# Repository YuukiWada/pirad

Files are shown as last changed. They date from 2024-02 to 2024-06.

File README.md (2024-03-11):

# PiRAD

## Overview
PiRAD is a radiation detector using Raspberry Pi. It allows for the acquisition of information for each photon of X-rays and gamma rays (energy and arrival time), as well as functions such as supplying high voltage for MPPCs (Multi-Pixel Photon Counters) and temperature compensation for MPPCs, all while being inexpensive and simple.

This software and design information are distributed under the GPL (GNU General Public License version 3). The developer bears no responsibility for any troubles, losses, or damages arising from the use of this software or design information.

## Usage
PiRAD consists of an analog circuit board that is stacked on the Raspberry Pi and software that runs on the Raspberry Pi.

### Things to prepare
- Raspberry Pi 4B+ (any memory capacity allowed)
- PiRAD board
- MPPC/SiPM, Scintillator, Coaxial cable
- AC adapter of 5 V and >2 A
- microSD card (16 GB or higher, Class 10 recommended)
- USB memory

### Circuit board
The `circuit` directory contains Gerber files and parts lists needed to fabricate a PCB board. Please use this information to produce the PCB board and mount the components on the board. The PCB board is a 4-layer board with dimensions of 105 mm x 56 mm. A disposable board is attached so that it can be fed into a chip mounter. V-cut is required. A reference marker for the chip mounter is also placed.

LT3482IUDTRPBF is used as the HV supplier chip. Please note that this chip has pads for surface mounting on the back side of the component, so placing components by a chip mounter may be required. In that case, it is necessary to manufacture a metal mask, which requires initial costs and is expensive if produced in small quantities. An effective method for small-volume production is to manufacture the boards without LT3482IUDTRPBF, and then manually mount it later manually. However, this is only possible if you have the technology to perform surface mounting using a heat gun and solder paste.

### Radiation detection section
This part is left to the user's choice. In the author's test environment, Hamamatsu's MPPC/SiPM S13360-6050CS is used, and a 1 x 1 x 1 cm GAGG scintillator is attached to the MPPC. The HV supply mounted on the circuit board has positive polarity, so supply voltage to the cathode and connect the anode to GND. In the author's environment, the MPPC is connected to the circuit board using a coaxial cable with an SMA terminal.

### Data Acquisition Software
The data acquisition software is stored in `scripts`. They consist of three languages: C, Python, and Ruby. Software operation has been confirmed on Raspberry Pi4 Model B and Raspberry Pi OS with Desktop 32-bit brookworm. 64-bit OS is not supported.

Please refer to `INSTALL.md` for how to set up the software.

### Radiation data acquisition
Once you have finished configuring the software, write the configuration file to a USB memory and insert it to the Raspberri Pi. Please refer to `INSTALL.md` for the configuration file settings.

After inserting the USB and turning on the Raspberry Pi, the PWR LED will light up. Observation can begin after the PWR LED turns on. By turning on the LOGGING slide switch, the USB memory will be mounted and observation will begin. If the USB memory cannot be read or is not correctly mounted, the LOG LED will blink twice.

If the USB memory is mounted successfully and the configuration file is also successfully read, the HV/LOG LED will light up and measurement will begin. If radiation is detected, the RAD LED will blink.

When a GPS module is connected and time synchronization is set, the GPS LED will light up while the time is synchronized by GPS acquisition.

To stop measurement, turn off the LOGGING slide switch. The HV/LOG LED will turn off within a few seconds. After that, the LOG LED will blink 5 times and the USB will be unmounted and you can safely remove it from the Raspberry Pi.

To shut down, press and hold the PWR OFF switch until the PWR LED turns off. Wait a few seconds for the shutdown process to complete. Please note that if you stop the power supply without performing the shutdown process, the SD card may not be read properly and you may not be able to start it up again.

### data format
Data is recorded in USB memory. Radiation data is recorded as text in CSV format, and the file name is the measurement start time (UTC). Inside the file is recorded as follows.
````
1710139818.021942
0.000070, 410
0.395692, 73
1.175464, 88
1.209030, 88
1.948140, 94
2.283456, 67
2.334519, 144
````
 The first line is the reference time (UNIXTIME), the second and subsequent lines correspond to the detected radiation event, the first column is the elapsed time (seconds) from the reference time, and the second column is the peak value (pulse height). Conversion from peak value to energy requires calibration using a radiation source, etc. The files are separated by day and are switched around 0:00 UTC (9:00 Japan Standard Time / JST).

HK (housekeeping) data is also saved with the recording start time as the file name, and is recorded as follows.

````
1706767240, 2024-02-01 06:00:40, 54.49946, 24.99, 30.12, 1011.96
1706767540, 2024-02-01 06:05:40, 54.49946, 24.83, 30.36, 1011.89
1706767840, 2024-02-01 06:10:40, 54.49946, 24.77, 30.31, 1011.87
1706768140, 2024-02-01 06:15:40, 54.49946, 24.91, 30.12, 1011.88
````
The first column is UNIXTIME, the second column is the corresponding time (UTC), the third column is the actual applied high voltage value, the fourth column is temperature, the fifth column is humidity, and the sixth column is atmospheric pressure. Note that if the HV's temperature compensation is turned off (including the case where the temperature sensor is not connected), the temperature, humidity, and pressure will not be recorded. Similarly, HK data files are separated by day, and are switched around 0:00 UTC (9:00 Japan time).

## Developer Information
Yuuki Wada (Assistant Professor, Department of Electrical, Electronic, and Infocommunications Engineering, Graduate School of Engineering, Osaka University)

## Update information
First edition: February 2, 2024
Second edition: March 11, 2024

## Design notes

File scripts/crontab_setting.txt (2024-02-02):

@reboot /usr/bin/python /home/pi/git/pirad/scripts/python/power.py
@reboot /usr/bin/python /home/pi/git/pirad/scripts/python/daq_control.py
@reboot /usr/bin/python /home/pi/git/pirad/scripts/python/gps_verification.py
@reboot /usr/bin/ruby /home/pi/git/pirad/scripts/ruby/time_set.rb

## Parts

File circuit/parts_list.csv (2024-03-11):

Manufacturer | Parts type | Model | Parts index | Quantity | Way to solder | Package | Specification
Kyocera | chip capacitor | 06031C103K4T4A | C1,C2,C3,C12,C14,C16,C18,C20,C22,C24,C26,C32,C33,C38 | 15 | SMD | 1608 | 0.01uF / 100V
AVX | chip capacitor | 06035A101JAT2A | C4 | 1 | SMD | 1608 | 100pF
Kyocera | chip capacitor | KGM15AR71H222KT | C5,C6 | 2 | SMD | 1608 | 2200pF
AVX | chip capacitor | 12063C225JAT2A | C11,C13,C15,C17,C19,C21,C23,C25,C28,C29,C31 | 11 | SMD | 3216 | 2.2uF
TDK | chip capacitor | C3216X7R2A224K115AA | C36,C37,C39 | 3 | SMD | 3216 | 0.22uF / 100V
AVX | chip capacitor | 06035C104JAT2A | C34,C35 | 2 | SMD | 1608 | 0.1uF / 50V
ROHM | LED | SML-D11YWT86 | LED1,LED2,LED3.LED4,LED5 | 5 | SMD | 1608
Bourns | variable register | 3296W-1-502LF | VR1 | 1 | DIP | RTRIM3296W | 5k / Attached to PCB surface
Laird-Signal Integrity Products | chip coil | TYA2520126R8M-10 | L3 | 1 | SMD | 1007 | 6.8uF
TDK | chip coil | MPZ1608S331ATA00 | L1,L2 | 2 | SMD | 1608
Diodes Incorporated | diode | 1N4148W-13-F | D1,D2 | 2 | SMD | SOD-123
Toshiba | MOSFET | SSM3K318R,LF | Q1 | 1 | SMD | SOT23
KOA | chip register | RK73H1JTTD51R0F | R1,R2,R7 | 3 | SMD | 1608 | 51
KOA | chip register | RK73H1JTTD1001F | R3,R8,R25 | 3 | SMD | 1608 | 1k
KOA | chip register | RK73H1JTTD1003F | R4,R5,R20,R21 | 4 | SMD | 1608 | 100k
KOA | chip register | RK73H1JTTD1002F | R6,R22 | 2 | SMD | 1608 | 10k
KOA | chip register | RK73H1JTTD3602F | R18 | 1 | SMD | 1608 | 36k
KOA | chip register | RK73H1JTTD1202F | R19 | 1 | SMD | 1608 | 12k
KOA | chip register | RK73H1JTTD1502F | R24 | 1 | SMD | 1608 | 15k
KOA | chip register | RK73H1JTTD1004F | R23 | 1 | SMD | 1608 | 1M
KOA | chip register | RK73H1JTTD3300F | R16,R17 | 2 | SMD | 1608 | 330
KOA | chip register | RK73H1JTTD1500F | R11,R12,R13,R14,R15 | 5 | SMD | 1608 | 150
AD | operational amplifier | ADA4891-2ARZ | U1,U2 | 2 | SMD | SOIC8
TI | operational amplifier | TL072CDR | U3 | 1 | SMD | SOIC8
Microchip | DAC | MCP4726A0T-E/CH | U4 | 1 | SMD | SOT23
Microchip | ADC | MCP3208-CI/SL | U5 | 1 | SMD | SOIC16
Adafruit Industries LLC | socket | 2222 | J2 | 1 | DIP |  | Attached to PCB back
Murata | DC-DC converter | CRE1S0505SC | U7 | 1 | DIP |  | Attached to PCB surface
E-Switch | Push switch | TL3301FF160QG | SW1 | 1 | SMD
C&K | Slide switch | JS202011JCQN | SW2 | 1 | SMD
LT | HV Supply | LT3482IUDTRPBF | U6 | 1 | SMD

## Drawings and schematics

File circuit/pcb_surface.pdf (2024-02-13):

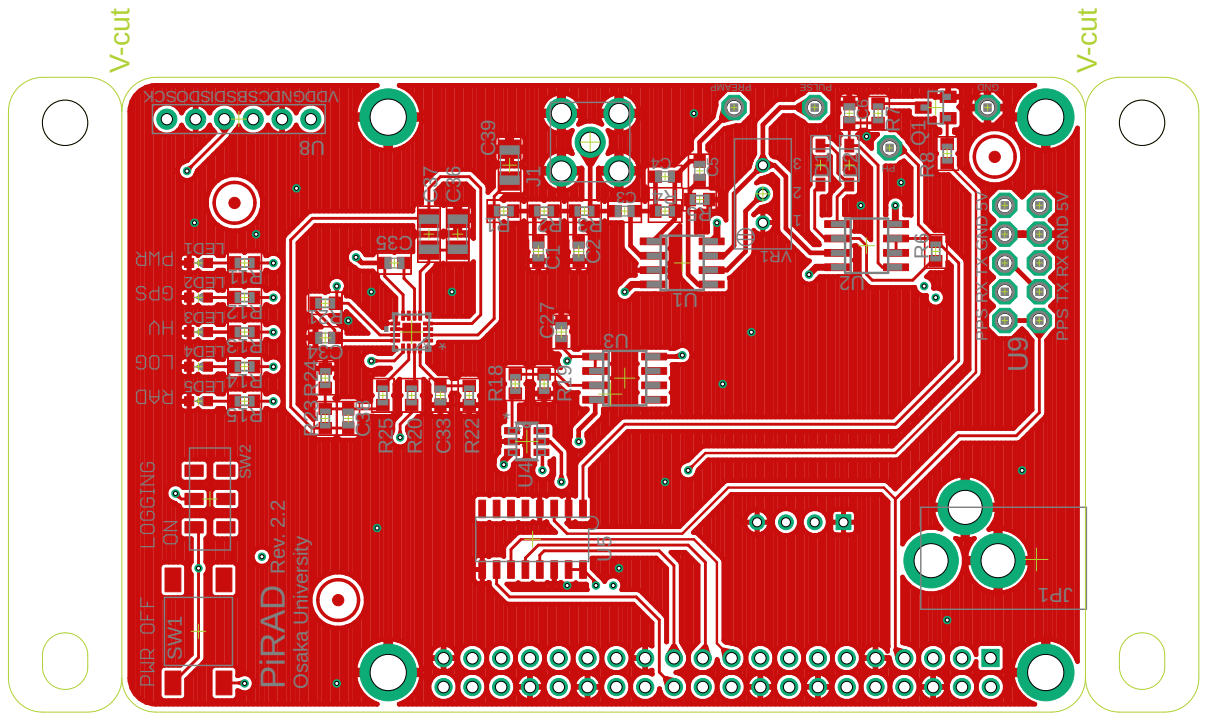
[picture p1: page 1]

1PJ 1 DEL 4 DEL 2 DEL 132 1 RV * KCSODSI DSBSCDNGDDV 5 DEL 3 DEL * * * 5V PPS RX TX GND PiRAD Rev. 2.2 Osaka University ESL UP DNG U9 U4 HP PPS RX TX GND 5V P MAERP 1 U 4 R SW1 SW2 11 R 41 R 21 R U5 4 C C5 5 R 2 U R6 D1 D2 C6 R7 Q18 U 51 R R23 R24 R22 R18 R19 3 U J1 1 R 2 R 3 R 3 C C2 C1 53 C C38 C33 R8 31 R R25 12 R 43 C R20 C36 C37 C39 C27 V-cut V-cut

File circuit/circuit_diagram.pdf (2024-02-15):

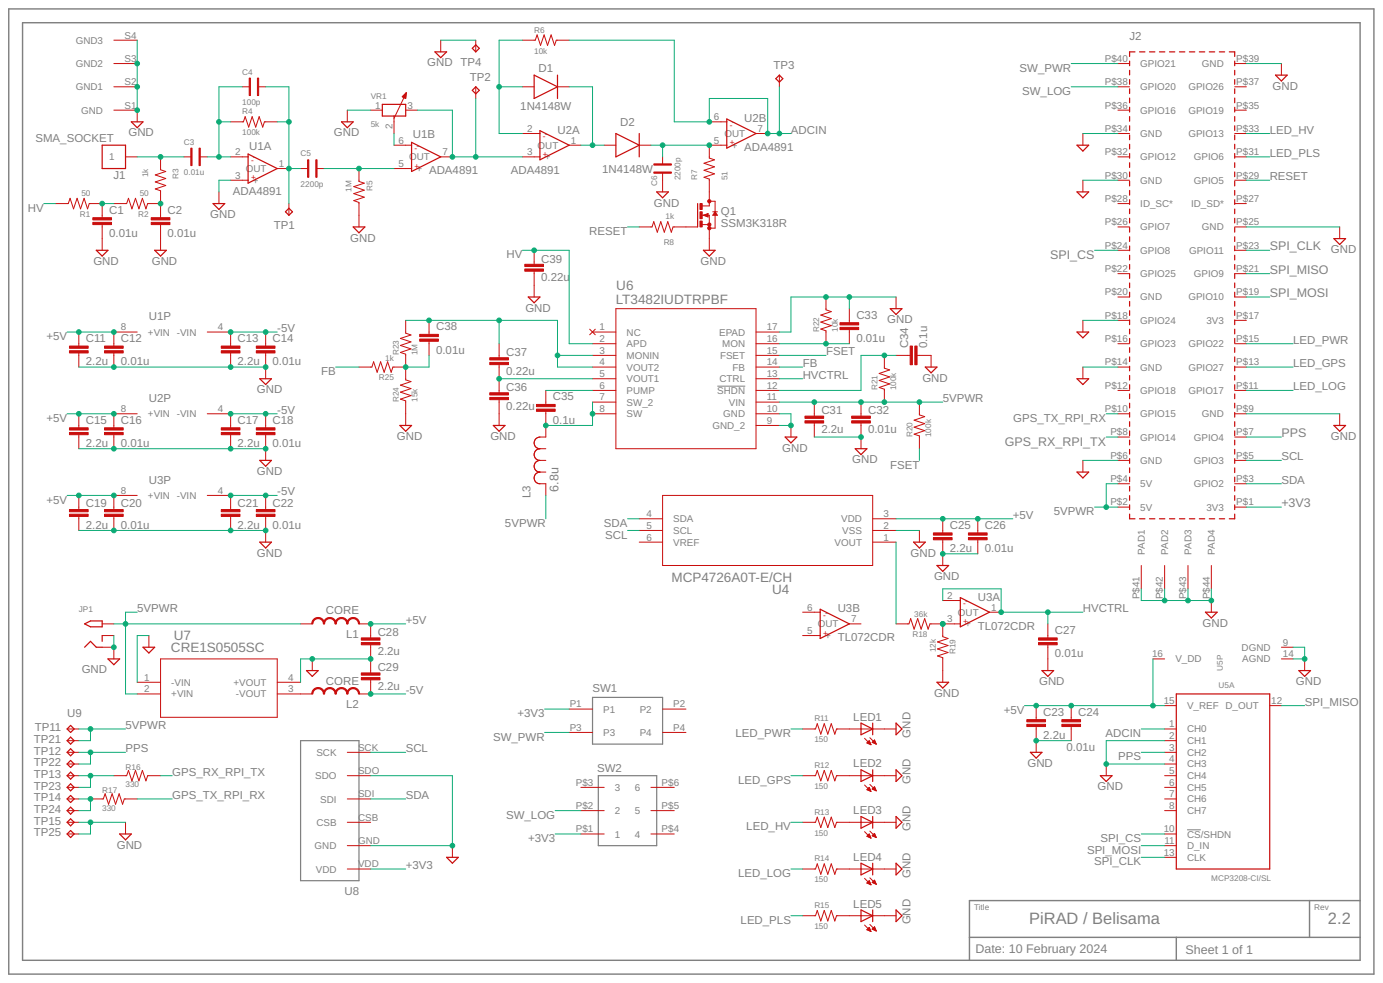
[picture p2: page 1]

Title PiRAD / Belisama | Rev2.2

Date: 10 February 2024 | Sheet 1 of 1

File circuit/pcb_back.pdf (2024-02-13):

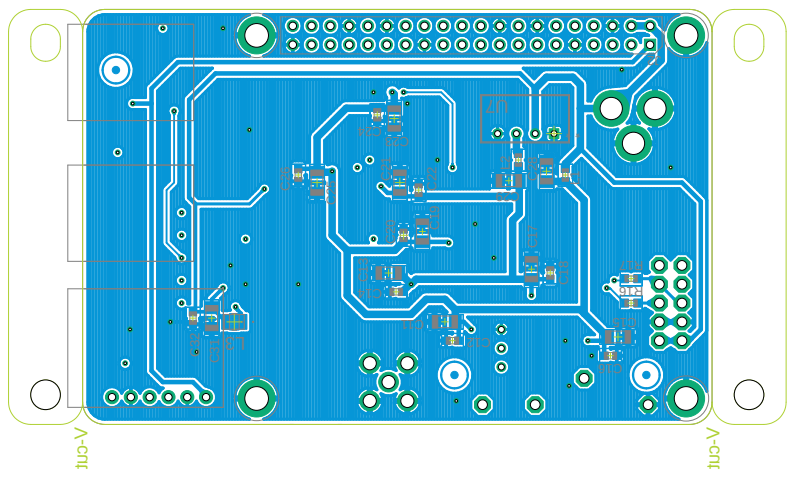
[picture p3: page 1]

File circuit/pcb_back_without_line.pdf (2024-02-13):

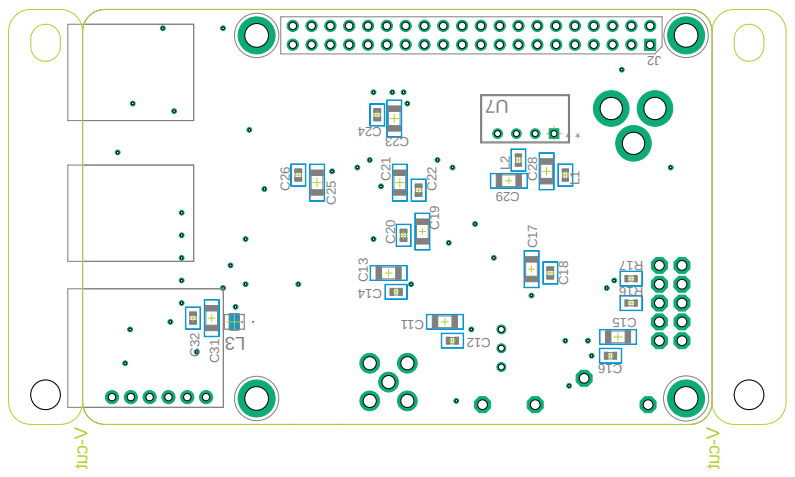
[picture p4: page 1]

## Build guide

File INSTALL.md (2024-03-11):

# How to install PiRAD software

## overview
This page describes how to install the software for Raspberry Pi used with PiRAD. Please note that this software is designed to operate on Raspberry Pi 4B+ and has not been tested on other Raspberry Pi versions. It also assumes an environment where you can access the Raspberry Pi via SSH.

## Things to prepare
- Raspberry Pi 4B+
- microSD card (16GB or higher, Class 10 recommended)
- Power supply for Raspberry Pi
- USB memory (formatted as FAT32)
- PC for configuration (the author uses macOS)

## Installation steps

### Preparing the SD card
First, write the OS for Raspberry Pi onto the SD card. Please use Raspberry Pi Imager for writing. Download and install the corresponding software from [here](https://www.raspberrypi.com/software/).

Insert the SD card into your PC and write the OS using Raspberry Pi Imager. Select Raspberry Pi 4 for Raspberry Pi Device and Raspberry Pi OS (32-bit) Debian Bookworm with the Raspberry Pi Desktop for OS. <span style="color: red;">Please be sure to select 32-bit. </span>

Raspberry Pi Imager

After selecting the SD card to write to, you will be asked about customizing the OS, so select "Change settings". Set your username and password on the settings screen. The username here is pi. Check "Enable SSH" on the Services tab. Once the settings are complete, start writing.

### OS preparation
Insert the SD card into the Raspberry Pi. Make sure it is connected to the network via wired LAN, and supply power to Raspberry Pi. Check the IP address assigned to Raspberry Pi on your router, etc.

Access the Raspberry Pi via SSH. An example command is below.
````
ssh pi@192.168.1.2
````
Usernames and IP addresses will vary depending on each configuration environment.

Next, configure GPIO settings. Enter
````
sudo raspi-config
````
 to open the settings screen. Select "Interface Options" and enable SPI, I2C, and Serial Port. You may also change the time zone, etc., if necessary. The time zone is set to GMT by default.

Although not required, it is a good idea to implement public key authentication.
````
mkdir ~/.ssh
cd ~/.ssh/
nano authorized_keys
````
If you enter the public key in `authorized_keys`, you will be able to log in without entering a password next time.

### Clone and install software
First, clone the source code from GitHub.
````
mkdir ~/git
cd ~/git
git clone https://github.com/YuukiWada/pirad
cd pirad
````

Compile the DAQ software.
````
cd ~/git/pirad/scripts/c_lang
bash ./make.sh
````
If no error messages are displayed, the compilation was successful.

Next, install the software required for the script to run.
````
sudo apt install -y ruby ruby-dev openssl libssl-dev
sudo apt install -y python3-smbus python3-smbus2 python3-bme280 python3-yaml
````

Next, configure the crontab. Add the contents of
````
~/git/pirad/scripts/crontab_setting.txt
````
to the crontab after opening crontab editor by the command below.

````
sudo crontab -e
````

Then restart Raspberry Pi.
````
sudo reboot
````
If the settings are successful, the PWR LED will turn on after rebooting.

### Preparing the USB memory
When using PiRAD on a daily basis, it reads configuration files from a USB memory and also writes observation data directly to the USB memory so that there is no need to access the Raspberry Pi. Please format the USB memory as FAT32.

Please store [config.yaml](https://github.com/YuukiWada/pirad/blob/main/scripts/config.yaml) in the top directory of the USB memory. The content of the configuration file is as below.
````
hv: 56.0
threshold: 10
compensation: off
temp_const: 0.054
hv_limit: 60
````
From the top, the HV setting value, DAQ threshold, presence or absence of temperature compensation for the high voltage supplied to the MPPC, MPPC temperature coefficient [V/degC], and HV upper limit are listed. If a temperature sensor is not installed, turn compensation off.

Insert the USB memory with the configuration file into the Raspberry Pi. If the USB memory is compatible with USB3.0, recommend inserting it into a USB3.0 port.

Turn on the LOGGING switch and wait a few seconds, the HV LED will turn on, followed by the LOG LED, and when radiation is observed, the RAD LED will blink.

### Setting up time synchronization using GPS
If a GPS module is connected, time synchronization using GPS is possible even offline.

Enter
````
sudo nano /boot/cmdline.txt
````
and comment out all the lines with # and instead
````
dwc_otg.lpm_enable=0 console=tty1 root=/dev/mmcblk0p2 rootfstype=ext4 elevator=deadline rootwait
````

Then, open
````
sudo nano /boot/config.txt
````
and add
````
init_uart_baud=9600
dtoverlay=pps-gpio,gpiopin=4,assert_falling_edge=true
````
in the last line. `assert_falling_edge` varies depending on the GPS module used; select true if PPS is a falling pulse (active low) and false if it is a rising pulse (active high).

Also, to recognize PPS input, execute the command below.
````
echo pps-gpio | sudo tee -a /etc/modules
````
Then,  restart Raspberry Pi.
````
sudo reboot
````

Install the required software after rebooting.
````
sudo apt install -y gpsd gpsd-clients pps-tools
````

Next is the gpsd settings. Open the configuration file as
````
sudo nano /etc/default/gpsd
````
and add
````
START_DAEMON="true"
DEVICES="/dev/ttyS0 /dev/pps0"
GPSD_OPTIONS="-n"
````
in the last line. Then, activate with the command below.
````
sudo systemctl enable gpsd.socket
````
If the GPS signal can be received, you can check the GPS signal with the following command.
````
gpsmon
sudo ppstest /dev/pps0
````

Install chrony as NTP software.
````
sudo apt -y install chrony
````

To change chrony settings, open the configuration file with
````
sudo nano /etc/chrony/chrony.conf
````
comment out
````
sourcedir /run/chrony-dhcp
````
with #, and add
````
refclock PPS /dev/pps0 lock NMEA refid GPS
````
in the last line. Then, beboot the system with

````
sudo systemctl restart chrony.service
````

You can check the NTP status with
````
chronyc sources -v
````
When the time is synchronized by GPS, the GPS LED lights up.

## Advanced settings

### I2C address ofTemperature sensor 
The temperature sensor is communicating via I2C. Operation has been confirmed using [Akizuki Denshi's AE-BME280] (https://akizukidenshi.com/catalog/g/g109421/). Its I2C address is 0x76.

If another BME280-based temperature sensor that supports I2C communication and a different I2C address are used, please rewrite address_temp in `~/git/pirad/scripts/python/control_hv.py`. Note that the DAC for HV control is also controlled by I2C communication and uses address 0x60, so duplicate addresses cannot be used.

### HV control parameters
The HV voltage is controlled by inputting a reference signal to the LT3482, an HV generation IC. The reference voltage is generated by the MCP4726, a 12-bit DAC chip with I2C communication, and is input to the LT3482 through a buffer. The control parameters of the DAC (maximum 12-bit = 4096) are adjusted according to the following formula to match the output voltage.
````
Channel = (HV+1.8821)/0.0213153
````
However, the output voltage and the voltage specified in the configuration file may change depending on the characteristics of mounted components such as resistors. Therefore, if you want to set more precise values, please calibrate and find the parameters, then change dac_const in `~/git/pirad/scripts/python/control_hv.py`. However, if an unexpected value is assigned, abnormal voltage may be supplied and cause the MPPC to malfunction, so please check the output voltage with a tester etc. before connecting.

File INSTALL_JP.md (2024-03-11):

# PiRAD ソフトウェアインストール方法

## 概要
本ページではPiRADで使用するRaspberry Pi用のソフトウェアのインストール方法を記述しています。なお本ソフトウェアはRaspberry Pi 4B+での動作を前提としており、他のRaspberry Piのバージョンでは動作確認を行っていません。またSSHでRaspberry Piにアクセスできる環境を前提としています。

## 準備するもの
- Raspberry Pi 4B+
- microSDカード (16GB以上のClass10を推奨)
- Raspberry Pi用の電源
- USBメモリー (FAT32でフォーマット)
- 設定用のPC (作者はmacOSを使用)

## インストールの手順

### SDカードの準備
まずSDカードにRaspberry Pi用のOSを書き込みます。書き込みにはRaspberry Pi Imagerを用います。[こちら](https://www.raspberrypi.com/software/) から対応するソフトウェアをダウンロードしてインストールします。

SDカードをPCに挿入して、Raspberry Pi ImagerでOSを書き込みます。Raspberry Pi DeviceはRaspberry Pi 4、OSはRaspberry Pi OS (32-bit) Debian Bookworm with the Raspberry Pi Desktopを選択します。<span style="color: red;">かならず32-bitを選択してください。</span>

Raspberry Pi Imager

書き込み先のSDカードを選択したあと、OSのカスタマイズについて聞かれるので、「設定を変更する」を選択します。設定画面でユーザー名とパスワードを設定します。ユーザー名はここではpiとします。サービスのタブで「SSHを有効化する」にチェックを入れてください。設定が終わったら書き込みを開始します。

### OSの準備
書き込みが終わったSDカードをRaspberry Piに差し込ます。有線LANでネットワークに接続されていることを確認し、Raspberry Piに電源を供給します。ルーター等でRaspberry Piに割り当てられたIPアドレスを確認します。

SSHでRaspberry Piにアクセスします。コマンド例は
```
ssh pi@192.168.1.2
```
です。ユーザー名やIPアドレスはそれぞれの設定環境で異なります。

続いてGPIOの設定を行います。
```
sudo raspi-config
```
と入力して設定画面を開きます。"Interface Options"を選択し、SPI、I2C、Serial Portを有効化しておきます。またこのとき必要であれば、タイムゾーンなども変更しておくとよいでしょう。タイムゾーンは初期設定ではGMTとなっています。

必須ではないものの、公開鍵認証を導入しておくとよいでしょう。
```
mkdir ~/.ssh
cd ~/.ssh/
nano authorized_keys
```
として、`authorized_keys`に公開鍵を記入しておくと、次回からパスワード入力なしでログインできるようになります。

### ソフトウェアのクローンとインストール
まずGitHubからソースコードをクローンします。
```
mkdir ~/git
cd ~/git
git clone https://github.com/YuukiWada/pirad
cd pirad
```

まずDAQソフトウェアをコンパイルします。
```
cd ~/git/pirad/scripts/c_lang
bash ./make.sh
```
特にエラーメッセージが表示されなければ、コンパイルは成功しています。

続いてスクリプトの動作に必要なソフトウェアをインストールします。
```
sudo apt install -y ruby ruby-dev openssl libssl-dev
sudo apt install -y python3-smbus python3-smbus2 python3-bme280 python3-yaml
```

さらにcrontabの設定を行います。
```
~/git/pirad/scripts/crontab_setting.txt
```
の内容を
```
sudo crontab -e
```
でcrontabの編集画面上に追記します。ここまでできたら
```
sudo reboot
```
で再起動します。設定がうまくいくと、再起動後にPWRのLEDが点灯します。

### USBメモリーの準備
PiRADは日常的に使用する際に、Raspberry Piにアクセスする必要がないよう、設定ファイルをUSBメモリーから読み出し、まだ観測データもUSBメモリーに直接書き込んでいます。USBメモリはFAT32でフォーマットしておいてください。

USBメモリーのトップディレクトリに[config.yaml](https://github.com/YuukiWada/pirad/blob/main/scripts/config.yaml)を格納してください。内容は
```
hv: 56.0
threshold: 10
compensation: off
temp_const: 0.054
hv_limit: 60
```
となっています。上からHVの設定値、DAQのスレッショルド、MPPCに供給する高電圧の温度補償の有無、MPPCの温度係数 [V/degC]、HVの上限値が記載されています。温度センサーが取り付けられていない場合はcompensationはoffにしてください。

設定ファイルを書き込んだUSBメモリーをRaspberry Piに挿してください。USBメモリーがUSB3.0に対応している場合は、USB3.0のポートに挿すことを推奨します。

LOGGINGのスイッチをONにして数秒待つと、HVのLED、続いてLOGのLEDが点灯し、放射線が観測されるとRADのLEDが点滅します。

### GPSによる時刻同期の設定
GPSモジュールを接続している場合、オフラインでもGPSによる時刻同期が可能となります。

```
sudo nano /boot/cmdline.txt
```
として記載されている行を#でコメントアウトし、代わりに
```
dwc_otg.lpm_enable=0 console=tty1 root=/dev/mmcblk0p2 rootfstype=ext4 elevator=deadline rootwait
```
と入力します。続いて
```
sudo nano /boot/config.txt
```
として、最後の行に
```
init_uart_baud=9600
dtoverlay=pps-gpio,gpiopin=4,assert_falling_edge=true
```
と記入します。assert_falling_edgeは使用するGPSモジュールによって異なり、PPSがたち下がりパルス (アクティブLow) の場合はtrue、立ち上がりパルスの場合はfalseを選択します。

またPPSの入力を認識させるため
```
echo pps-gpio | sudo tee -a /etc/modules
```
と実行します。ここで一度再起動します。
```
sudo reboot
```

再起動後に必要なソフトウェアをインストールします。
```
sudo apt install -y gpsd gpsd-clients pps-tools
```

続いてgpsdの設定です。
```
sudo nano /etc/default/gpsd
```
として設定ファイルを開き、最後の行に
```
START_DAEMON="true"
DEVICES="/dev/ttyS0 /dev/pps0"
GPSD_OPTIONS="-n"
```
と追記し、
```
sudo systemctl enable gpsd.socket
```
として有効化します。GPS信号が受信できていれば
```
gpsmon
sudo ppstest /dev/pps0
```
といったコマンドでGPS信号の確認ができます。

NTPのソフトウェアとしてchronyをインストールします。
```
sudo apt -y install chrony
```

chronyの設定を変更するため
```
sudo nano /etc/chrony/chrony.conf
```
で設定ファイルを開きます。
```
sourcedir /run/chrony-dhcp
```
を#でコメントアウトし、
```
refclock PPS /dev/pps0 lock NMEA refid GPS
```
を追記します。
```
sudo systemctl restart chrony.service
```
でシステムを再起動します。

```
chronyc sources -v
```
でNTPの状況を確認できます。GPSによる時刻同期がされた場合はGPSのLEDが点灯します。

## 高度な設定

### 温度センサーのI2Cアドレス
温度センサーはI2Cで通信しています。動作確認は[秋月電子のAE-BME280](https://akizukidenshi.com/catalog/g/g109421/)で行っており、I2Cアドレスは0x76を選択しています。

他のBME280ベースのI2C通信対応の温度センサーを使用する場合で、異なるI2Cアドレスを使用する場合は、`~/git/pirad/scripts/python/control_hv.py`のaddress_tempを書き換えてください。なおHV制御用のDACもI2C通信で制御しており、そのアドレスは0x60を使用していますので、重複したアドレスを使用することはできません。

### HV制御のパラメータ
HVの電圧はHV生成用のICであるLT3482にリファレンス信号を入力して制御しています。リファレンス電圧はI2C通信対応の12-bit DACチップであるMCP4726で生成し、バッファーを通じてLT3482に入力されています。DACの制御パラメータ (最大12-bit = 4096) は出力電圧と一致するように以下の式に調整されています。
```
Channel = (HV+1.8821)/0.0213153
```
ただし出力電圧と設定ファイルでの指定電圧は抵抗など実装部品のKu世用特性によって変化することがあります。そのため、より精密な値を設定したい場合は、キャリブレーションしてパラメータを求めたうえで、`~/git/pirad/scripts/python/control_hv.py`のdac_constを変更してください。ただし予期せぬ値が代入された場合、高電圧が印加され、MPPCが故障する原因になりますので、接続する前にテスター等で出力電圧を確認してください。

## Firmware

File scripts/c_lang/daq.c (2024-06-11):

#include <pigpio.h>
#include <unistd.h>
#include <stdio.h>
#include <stdlib.h>
#include <signal.h>
#include <sys/time.h>

void signal_handler(int signum)
{
  gpioTerminate();
  exit(1);
}

int main(int argc, char *argv[]){
  
  int threshold = atoi(argv[1]);
  int pin_reset = 5;
  int pin_led = 6;
  int spi_device = 0;
  int baud = 500000;
  int spi_flag = 0;
  const int data_length = 3;
  char conf[data_length];
  char adc[data_length];

  signal(SIGINT, signal_handler);
  //signal(SIGTERM, signal_handler);
  
  gpioInitialise();
  gpioSetMode(pin_reset, PI_OUTPUT);
  gpioSetMode(pin_led, PI_OUTPUT);
  int handle = spiOpen(spi_device, baud, spi_flag);

  conf[0] = 0b0000011;
  conf[1] = 0b0000000;
  conf[2] = 0b0000000;

  struct timeval time;
  gettimeofday(&time, NULL);
  double time_start = time.tv_sec+time.tv_usec/1000000.0;
  printf("%f\n",time_start);

  while (1){
    spiXfer(handle, conf, adc, data_length);
    int value = ((adc[1]&0x0f)<<8) | adc[2];
    if (value>threshold){
      gettimeofday(&time, NULL);
      double time_now = time.tv_sec+time.tv_usec/1000000.0;
      double delta_time = time_now-time_start;
      printf("%f, %i\n",delta_time,value);
      
      gpioWrite(pin_reset, 1);
      usleep(1);
      gpioWrite(pin_reset, 0);
      gpioWrite(pin_led, 1);
    }
  }
  return 0 ;
}

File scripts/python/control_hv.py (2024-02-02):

#! /usr/bin/env python
# -*- coding: utf-8 -*-
import datetime
import smbus
import smbus2
import bme280
import sys
import time
import RPi.GPIO as GPIO

output_dir = sys.argv[1]
hv_ref = float(sys.argv[2])
comp_sw = int(sys.argv[3])
const_temp = float(sys.argv[4])
hv_limit = float(sys.argv[5])

interval = 1800 # sec
interval_measure = 300 # sec
temp_base = 25.0

i2c = smbus.SMBus(1)
address_temp = 0x76
address_dac = 0x60
dac_const = [1.8821,0.0213153]

GPIO.setwarnings(False)
GPIO.setmode(GPIO.BCM)
GPIO.setup(13, GPIO.OUT)

hv = 0
hv_previous = 0

if comp_sw==1:
  bme280.load_calibration_params(smbus2.SMBus(1),address_temp)
  max_count = round(interval/interval_measure)
  count = max_count-1

  while True:
    try:
      data_all = bme280.sample(smbus2.SMBus(1),address_temp)
      temp = round(data_all.temperature,2)
      humid = round(data_all.humidity,2)
      press = round(data_all.pressure,2)
      hv = hv_ref + (temp-temp_base)*const_temp
      if (hv>hv_limit) or (hv<0):
        hv = 0
    except:
      temp = False
      humid = False
      press = False
      hv = 0
    ut = round(time.time())
    dt = datetime.datetime.fromtimestamp(ut).strftime("%Y-%m-%d %H:%M:%S")
    output_file = "{}/hk_{}.dat".format(output_dir,datetime.datetime.fromtimestamp(ut).strftime("%Y%m%d"))
    if (count==max_count-1) or (hv==0):
      with open(output_file, "a") as f:
        f.write("{}, {}, {}, {}, {}, {}\n".format(ut,dt,hv,temp,humid,press))
        print("{}, {}, {}, {}, {}, {}".format(ut,dt,hv,temp,humid,press))
      hv_command = round((hv+dac_const[0])/dac_const[1])
      if hv_command<0:
        hv_command = 0
      command = [(hv_command&0xff0)>>4, (hv_command&0x00f)<<4]
      i2c.write_i2c_block_data(address_dac, 0x40, command)
      print("HV changed.")
      if hv>0:
        GPIO.output(13, 1)
      else:
        GPIO.output(13, 0)
      count = 0
      hv_previous = hv
      time.sleep(interval_measure)
    else:
      with open(output_file, "a") as f:
        f.write("{}, {}, {}, {}, {}, {}\n".format(ut,dt,hv_previous,temp,humid,press))
        print("{}, {}, {}, {}, {}, {}".format(ut,dt,hv_previous,temp,humid,press))
      count+=1
      time.sleep(interval_measure)
      
else:
  max_count = round(interval/interval_measure)
  count = max_count-1

  while True:
    ut = round(time.time())
    dt = datetime.datetime.fromtimestamp(ut).strftime("%Y-%m-%d %H:%M:%S")
    hv = hv_ref
    if (hv>hv_limit) or (hv<0):
      hv = 0
    output_file = "{}/hk_{}.dat".format(output_dir,datetime.datetime.fromtimestamp(ut).strftime("%Y%m%d"))
    with open(output_file, "a") as f:
      f.write("{}, {}, {}\n".format(ut,dt,hv))
      print("{}, {}, {}".format(ut,dt,hv))
    if (count==max_count-1) or (hv==0):
      hv_command = round((hv+dac_const[0])/dac_const[1])
      if hv_command<0:
        hv_command = 0
      command = [(hv_command&0xff0)>>4, (hv_command&0x00f)<<4]
      i2c.write_i2c_block_data(address_dac, 0x40, command)
      print("HV changed.")
      if hv>0:
        GPIO.output(13, 1)
      else:
        GPIO.output(13, 0)
      count = 0
      time.sleep(interval_measure)
    else:
      count += 1
      time.sleep(interval_measure)
      

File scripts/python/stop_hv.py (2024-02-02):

#! /usr/bin/env python
# -*- coding: utf-8 -*-
import smbus
import smbus2
import bme280
import datetime
import sys
import time
import RPi.GPIO as GPIO

output_dir = sys.argv[1]
comp_sw = int(sys.argv[2])

i2c = smbus.SMBus(1)
address_temp = 0x76
address_dac = 0x60
dac_const = [1.8821,0.0213153]

hv = 0

GPIO.setwarnings(False)
GPIO.setmode(GPIO.BCM)
GPIO.setup(13, GPIO.OUT)

if comp_sw==1:
  bme280.load_calibration_params(smbus2.SMBus(1),address_temp)
  try:
    hv = 0
    data_all = bme280.sample(smbus2.SMBus(1),address_temp)
    temp = round(data_all.temperature,2)
    humid = round(data_all.humidity,2)
    press = round(data_all.pressure,2)    
  except:
    hv = 0
    temp = -100
    humid = -100
    press = -100
  ut = round(time.time())
  dt = datetime.datetime.fromtimestamp(ut).strftime("%Y-%m-%d %H:%M:%S")
  output_file = "{}/hk_{}.dat".format(output_dir,datetime.datetime.fromtimestamp(ut).strftime("%Y%m%d"))
  with open(output_file, "a") as f:
    f.write("{}, {}, {}, {}, {}, {}\n".format(ut,dt,hv,temp,humid,press))
  i2c.write_i2c_block_data(address_dac, 0x40, [0,0])
  GPIO.output(13, 0)
      
else:
  ut = round(time.time())
  dt = datetime.datetime.fromtimestamp(ut).strftime("%Y-%m-%d %H:%M:%S")
  hv = 0
  output_file = "{}/hk_{}.dat".format(output_dir,datetime.datetime.fromtimestamp(ut).strftime("%Y%m%d"))
  with open(output_file, "a") as f:
    f.write("{}, {}, {}\n".format(ut,dt,hv))
  i2c.write_i2c_block_data(address_dac, 0x40, [0,0])
  GPIO.output(13, 0)

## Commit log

2024-02-01 Optimised for Raspberry Pi 4
2024-02-02 Added circuit diagram
    [parts_list.xlsx, pirad_Legend_Bot.GBO, pirad_Legend_Top.GTO, pirad_Paste_Bot.GBP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]
2024-02-13 Circuit updated Ver2.2
    [pirad_Legend_Top.GTO, pirad_copper_l1.GTL, pirad_copper_l4.GBL, pirad_drill.XLN]
2024-03-11 Added partslist
    [parts_list.csv]
